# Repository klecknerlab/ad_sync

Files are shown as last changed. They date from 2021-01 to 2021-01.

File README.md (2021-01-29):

# ad_sync
Hardware and software design for a USB-based analog/digital synchronizer board.  Developed by the MUVI and Kleckner Labs at UC Merced.

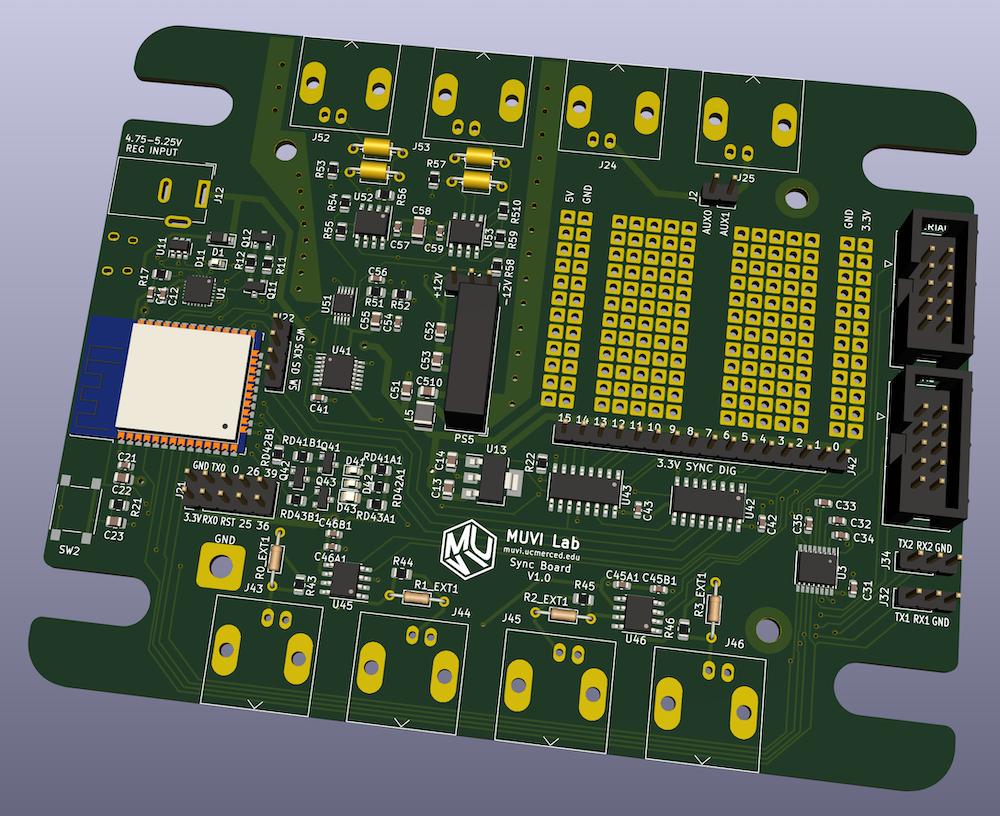
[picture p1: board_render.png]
Board Render


## Description
This project is intended to solve a specific problem: synchronizing a laser scanner and camera setup for 3D volumetric imaging.
To do this, it outputs hardware synchronized digital and analog signals.
The hardware works by converting a single digital bit stream from the on board ESP32 processor to a series of shift registers and a digital-to-analog converter (with ± 10V range).
The update rate is tunable from 30 Hz to 700 kHz, with a ~10 PPM accurate clock (provided by the APLL clock on the ESP32).

The hardware, firmware and software required to run the board is all stored in this repository, with an Apache license.
If you would like to fabricate, modify, or just use these boards, get in touch!

## Features
* 16 synchronized digital outputs.  Four are converted to 5 V and output on external BNC or header pin connections
* 2 synchronized analog outputs, output on BNC or header pins
* 2 auxiliary serial ports (RS-232 levels), tunneled through the main connection, and which can be used to control additional devices
* An RGB output LED, controllable through software, to be used as an indicator light
* A small on-board prototyping area, to add additional functionality
* Pin headers for various on board signals, including unused GPIO ports on the microcontroller.  (These are not usable without a firmware modification.)
* Everything is controlled through a USB port *or* Bluetooth conncection, with simple serial commands.  (To enable bluetooth, use `set_bt_name.py`.)
* In the future, a firmware update may also provide a wifi connection option; the microcontroller is capable of this but the feature has not been coded)

## Project Progress
* [x] Initial board schematics
* [x] Fabricate test hardware
* [x] Feature complete firmware
* [x] USB communications
* [x] Python driver
* [ ] Wifi connection
* [x] Bluetooth connection
* [x] Aux. serial port connections
* [x] Experimental testing and validation
* [x] Synchronizer GUI

## Contents
This project contains four directories:
* `hardware`: the hardware schematics and PCB layout.
* `hardware_fab`: the PCB design output files, which can be sent directly to a board fabricator.
* `firmware`: the Arduino/C++ firmware for the driver board, as a PlatformIO project.  (Note: currently in alpha status.)
* `ad_sync`: a Python library to interface with the board through USB. (Note: currently empty.)

## Python Interface
The device is most easily controlled with the provided Python library.
All of the functions are illustrated in `test.py`, located in this directory.

All of the functions in the communication protocol (described below), also have a corresponding python method with a similar or identical name.

On some OS's you may need to install drivers for the USB chip on the board ([Sillabs CP2104](https://www.silabs.com/developers/usb-to-uart-bridge-vcp-drivers).)

## Description of Synchronized Outputs
The synchronized outputs are fed from an internal memory of up to 16384 samples.
Each sample is a 32 bit unsigned integer.
The high 16 bits are the digital channels, and the low 16 bits are an analog sample.
Typically, the analog sample should contain the full data range (0-65535), and can be dynamically scaled as the signal is generated.
(This way you don't need to upload entirely new data to offset or rescale the analog signal.)

To specify an output, you first upload an arbitrary amount of data (in Python, use the `write_ad` method).
You then tell the device where to read from in memory, by specifying a start address and number of samples (`addr` method).
Additionally, you can specify the output rate in samples/s (`rate` method).

Finally, you can specify that certain digital channels are triggered.
Triggered channels will remain low until a trigger is specified (`trigger` method).
Note that the trigger always starts on the beginning of an output cycle, and can be for one or more cycles.

## Communication Protocol
Although the Python library is convenient, it is also possible to talk to the board directly with serial commands through the USB interface (and eventually: bluetooth and wifi, which will use a serial bridge).

**Command structure:** one to three "words", at most four letters each, followed by 0-3 integers.  Some commands are also followed by arbitrary length binary data.  
All commands are terminated with a linefeed character (`⏎`; this is equivalent to `"\n"` in Python or C).  

The format for binary appended data is `>[number of bytes]>[binary data]`, and should followed by a line feed character.

Note that if the word is longer than 4 letters the extra letters are ignored.
In other words `SYNC AVAIL` is the same as `SYNC AVAI` (or even `SYNC AVAILABLE` if you prefer).  
Lower case letters are converted to upper case internally (i.e. `SynC AvAiXXX` is also equivalent.)

Unless specified otherwise, commands return `ok.⏎` on success.
Error strings will always begin with `ERROR:` and end with `⏎`.

*Note:* For the command words `ANA0`, `ANA1`, `SER1`, and `SER2` there is no space between the letters and number -- this number is part of the command, not an argument!
(If you're wondering why the serial numbering starts with 1: this is because serial 0 is the USB connection.)

### List of Serial Commands
Parameters are specified in square brackets, and correspond to unsigned integers (exception: commands which have an `ON/OFF` option).

**Misc Commands**
* `*IDN⏎`: Returns the identification string for the synchronizer.  (Presently: `USB analog/digital synchronizer (version 1.0)⏎`)
* `LED [r] [g] [b]⏎`: Set the color of the RGB indicator LED.  Each value should be 0-255, and the output is gamma corrected.

**Sync Output Commands**
* `SYNC STAT⏎`: Outputs statistics on the sync DMA buffer output.  Used for debugging, but shouldn't normally be needed.
* `SYNC WRITE [addr] >[n]>[binary data]⏎`: Write synchronous data starting at indicated address (addr < 16384).  
    - Each data point is four bytes, or a uint32.  The highest two bytes are the digital outputs for that sample and the lowest two bytes are the analog signal.  Note that the microcontroller is little-endian, thus the byte order should be `[analog low][analog high][digital low][digital high]`.  
    - The data written should have a length which is a multiple of 4 bytes, but this is not enforced!  (A warning will be issued if this condition is not met.)  There is no padding between samples, and you can upload as many as you want at once.
    - Ideally, the analog data should span the full 0--65535 range.  The amplitude and offset of the output can be controlled with the `ANA[0/1] SCALE` command, so that you don't have to reupload data to rescale the analog output.
* `SYNC [START/STOP]⏎`:
    - Start/stop the synchronous digital outputs by enabling or disabling the shift register outputs and stopping the sync updates.
    - When stopped, the analog channels will default to the values set by `ANA[0/1] SET`.
* `SYNC MODE [analog mode] [digital mode (optional)]⏎`: Set the mode of the sync output.  
	- Analog mode options:
		- `0`: No sync analog output; each channel goes to the default (set w/ `ANA[0/1] SET`)
		- `1`: Analog 0 streams from sync data, analog 1 fixed value (default)
		- `2`: Analog 1 streams from sync data, analog 0 fixed value
		- `3`: Both channels stream, alternating updates.  Even sync data addresses go to analog 0, odd address to analog 1.  Note that this halves the update rate of each channel, relative to the digital signals.
	- Digital mode options:
		- `0`: All 16 outputs derived from sync data (default)
		- `1`: "Or" mode.  Channels 0-7 are logical "or"ed with channels 8-15.  8-15 have the normal output.  (Can be used to superimpose triggered and non-triggered signals.)
        - `2`: "Swap" mode.  Channels 0-7 swapped with 8-15.  (Can be used to switch the
            outputs w/o a reupload.)
        - `3': "Swap-Or" mode.  Apply the swap and then the or operation.
* `SYNC ADDR [addr] [count]⏎`: Change the start address and number of data points for a period of the sync output.
* `SYNC ADDR⏎`: Returns the current sync mode (`SYNC CYCLE [addr] [count]⏎`)
* `SYNC RATE [rate Hz] [rate mHz (optional)]⏎`:
    - Change the synchronous output rate, specified in Hz, with any optional millihertz addition.  (i.e. 100.5 Hz would be specified as `SYNC RATE 100 005⏎` or `SYNC RATE 100 5⏎`.)  Valid values are from 30 to 700000.  
    - Replies with `SYNC RATE = [samples/s] Hz⏎`.  Note that [samples/s] will here be floating point, and reflects the actual frequency as set by the device (will likely be *slightly* different than the requested value)
    - Accuracy/precision is ~10 PPM, as determined by main clock accuracy.
* `ANA[0/1] SCALE [scale] [offset]⏎`:
    - Change the output scale and offset of this channel.  Each scale/offset should be from 0-65536 and covers the range of -10 to 10 V.  
    - `scale` indicates the peak to peak amplitude of the signal (65536 = 20 V peak-to-peak, 3277 = 1.0000 V peak-to-peak)
    - `offset` is the minimum value of the signal (0 = -10 V, 65536 = 10V, 32768 = 0V.)  
    - *Note:* the above scaling assumes the input waveform goes from 0-65535 in the sync data.  If it does not, it will be proportionally smaller.
* `ANA[0/1] SET [value]⏎`:
    - Directly set the analog output value for one of the channels (0=-10V, 65536 = +10V).  No scaling or offset is applied.  
    - *Note 1:* Command ignored if this channel is currently updating synchronously.  
    - *Note 2:* Updating while the sync is running on the other channel will introduce a one sample skip in the output of the synced channel.

**Serial Commands**
* `SER[1/2] WRITE >[n]>[binary data]⏎`: Write `n` bytes to serial port 1/2.  Replies with: `Wrote [n] bytes of data to serial [1/2].⏎`
* `SER[1/2] READ [n (optional)]⏎`:
    - Read at most `n` bytes of data from serial port 1/2  
    - If `n` is not specified (or `n` is greater than the amount of available data), return all available data.  
    - Call is non-blocking: it will not wait for data to be available
    - Reply format is `>[n]>[n bytes of binary]⏎`  
* `SER[1/2] AVAIL⏎`: Return the number of bytes available to be read at that serial port.  Reply format: `[n]⏎`
* `SER[1/2] FLUSH⏎`: Flush the read buffer for a serial port.
* `SER[1/2] RATE [baud rate]⏎`:
    - Set the baud rate for a serial port  
    - The serial format is always 8 bits with a start and stop bit.  (This could be changed by altering the firmware, if needed.)
    - *Note:* Changing the Baud rate of Serial Port 1 will cause an output glitch on the sync outputs.  Unfortunately this is a hardware bug on the microcontroller, which is not correctable!

**Trigger Commands**
* `TRIGER MASK [bit mask]⏎`: A bit mask indicated if each digital output channel is triggered.  Triggered channels output low until triggered.
* `TRIGER [cycles (optional)]⏎`: Activate the trigger for the specified number of cycles.  `cycles=1` is the default.  Note that there may be a delay of up to 256 samples in outputting a triggered signal, due to the output buffering.  Also, triggers always begin at the beginning of a cycle.

**Bluetooth Commands**
* `BLUETOOTH >[n]>[bluetooth name]⏎`:
    - Set the name of the bluetooth device, and enables it
    - Name will be saved to internal flash storage, and will remain after a reboot
    - Name needs to be sent as binary, should be <= 64 bytes (or an error is raised)
    - Replies with `Bluetooth enabled with name: [bluetooth name]⏎`
    - Setting the name to an empty string disables the device (e.g. `BLUETOOTH⏎`)

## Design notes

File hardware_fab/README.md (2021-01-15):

This directory contains the files for fabricating the physical board.
The original version (V1, V1 rev. 2) was fabricated using [JLCPCB](https://jlcpcb.com/), which provides a low cost PCB assembly service.
(5 boards + components ~ $120.)
**If you are going to have these fabricated, you should use the rev. 2 version, which fixes a problem with one of the chip connections!**

All files needed to fabricate the board are in this directory, note that there are two versions of the component placement file -- the one ending in `pos-fixed.csv` has the rotations fixed to JLCPCB's specifications, and this is the file you should use for this board manufacturer.  The similarly named file without the `-fixed` is the raw part placement output from KiCad.

In addition to the surface mount components (which can be installed by JLCPCB), there are a number of through hole components which need to be manually attached.
These are listed below, along with links to Digikey or Amazon to purchase them.
Note that many of these are optional.  
Also not listed are headers for connecting to the peripherial outputs near the center of the board: these are all standard 0.1" pin headers.

**Mandatory Components:**
* Micro-USB connector (1 per board: [Amphenol 10103594-0001LF](https://www.digikey.com/en/products/detail/amphenol-icc-fci/10103594-0001LF/2350351?s=N4IgTCBcDaIIwAZEGYCsBOALCAugXyA))
* DC-DC converter (1 per board: [CUI PDME1-S5-D12-S](https://www.digikey.com/en/products/detail/cui-inc/PDME1-S5-D12-S/10229857) or equivalent)

**Output Connectors:**  (Note: the 8 main outputs are designed to be BNC jacks, but the holes on the board also support attaching a 0.1" header.)
* BNC (up to 8 per board: [TE connectivity 1-1337543-0](https://www.digikey.com/en/products/detail/te-connectivity-amp-connectors/1-1337543-0/1755940) or equivalent.)
* Alternate: 2 pin polarized right angle header (up to 8 per board: [Adam Tech LHA-02-TRB](https://www.digikey.com/en/products/detail/adam-tech/LHA-02-TRB/9830340)) (Mating plug: [Adam Tech MTD-A-02-D-2](https://www.digikey.com/en/products/detail/adam-tech/MTD-A-02-D-2/9830865))
* Serial outputs: 10 pin IDC connectors (up to 2 per board: [On Shore 302-S101](https://www.digikey.com/en/products/detail/on-shore-technology-inc/302-S101/2178422))
* IDC -> DB9 serial connectors (2 per board: [standard DB9 to 10 pin motherboard connector](https://www.amazon.com/CablesOnline-10-Pin-Motherboard-Adapter-AD-I01/dp/B077F2WDZ7/))

**Stand-offs:**
* 1/4"-20 x 1" for mounting the board to an optical table (4 per board: [Essentra 15TSP035](https://www.digikey.com/en/products/detail/essentra-components/15TSP035/11639005))
* 4-40 x 5/8" for mounting a protective top panel (4 per board: [RAF 2059-440-AL](https://www.digikey.com/en/products/detail/raf-electronic-hardware/2059-440-AL/7680412))

**Misc. Optional:**
* Power jack -- only needed if you aren't powering through USB (1 per board: [Wurth 	
694106301002](https://www.digikey.com/en/products/detail/w%C3%BCrth-elektronik/694106301002/5047522))
* Filter capacitors: the analog output amplifiers have empty slots for a through hole capacitor.  
The amplifier resistor is 120 kOhm, so 100 pF gives a -3dB frequency of 13.3 KHz.  
There is already 30 pF attached to the output (CF3/CF13) giving a 44 kHz cutoff; if higher speeds are required you could remove these resistors, but this is not recommended.
If you would like to provide additional filtering, a capacitor could be attachd to CF2/CF12.

* Output resistors: the digital outputs come with a surface mount 50 Ohm resistor installed.  If you would like a different output resistance, you can remove this resistor and add a through hole resistor next to the BNC output.  In most cases this should not be needed.

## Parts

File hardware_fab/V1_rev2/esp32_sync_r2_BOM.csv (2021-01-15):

Comment | Designator | Footprint | LCSC
0.1UF/50V | C11,C21,C31,C32,C33,C34,C35,C41,C42,C43,C44,C46,C54,C57,C59 | Capacitor_SMD:C_0603_1608Metric | C14663
4.7UF/16V | C12,C45,C47 | Capacitor_SMD:C_0603_1608Metric | C19666
22UF/25V | C13,C14,C22,C52,C53 | Capacitor_SMD:C_0805_2012Metric | C45783
1UF/50V | C23 | Capacitor_SMD:C_0805_2012Metric | C28323
4.7UF/25V | C51,C510 | Capacitor_SMD:C_0805_2012Metric | C1779
100PF/50V | C55 | Capacitor_SMD:C_0805_2012Metric | C1790
0.22UF/25V | C56 | Capacitor_SMD:C_0603_1608Metric | C21120
10UF/50V | C58 | Capacitor_SMD:C_1206_3216Metric | C13585
100pF | CF1,CF2,CF11,CF12 | Capacitor_THT:C_Axial_L3.8mm_D2.6mm_P7.50mm_Horizontal
30PF/50V | CF3,CF13 | Capacitor_SMD:C_0603_1608Metric | C22397
B5819W | D1 | Diode_SMD:D_SOD-123 | C8598
RED | D11,D41 | LED_SMD:LED_0603_1608Metric | C2286
GREEN | D42,D44 | LED_SMD:LED_0603_1608Metric | C72043
BLUE | D43 | LED_SMD:LED_0805_2012Metric | C2293
USB_B_Micro | J11 | Connector_USB:USB_Micro-B_Amphenol_10103594-0001LF_Horizontal
Barrel_Jack | J12 | Connector_BarrelJack:BarrelJack_Wuerth_6941xx301002
Conn_01x02_Male | J2 | Connector_PinHeader_2.54mm:PinHeader_1x02_P2.54mm_Vertical
GPIO | J21 | Connector_PinHeader_2.54mm:PinHeader_2x05_P2.54mm_Vertical
I2S | J22 | Connector_PinHeader_2.54mm:PinHeader_1x05_P2.54mm_Vertical
AUX0 | J24 | Connector_Coaxial:BNC_Amphenol_B6252HB-NPP3G-50_Horizontal
AUX1 | J25 | Connector_Coaxial:BNC_Amphenol_B6252HB-NPP3G-50_Horizontal
IDC SER | J31,J33 | Connector_IDC:IDC-Header_2x05_P2.54mm_Vertical
SER1 | J32 | Connector_PinHeader_2.54mm:PinHeader_1x03_P2.54mm_Vertical
SER2 | J34 | Connector_PinHeader_2.54mm:PinHeader_1x03_P2.54mm_Vertical
DS_3.3V | J42 | Connector_PinHeader_2.54mm:PinHeader_1x16_P2.54mm_Vertical
DS0_EXT | J43 | Connector_Coaxial:BNC_Amphenol_B6252HB-NPP3G-50_Horizontal
DS1_EXT | J44 | Connector_Coaxial:BNC_Amphenol_B6252HB-NPP3G-50_Horizontal
DS2_EXT | J45 | Connector_Coaxial:BNC_Amphenol_B6252HB-NPP3G-50_Horizontal
DS3_EXT | J46 | Connector_Coaxial:BNC_Amphenol_B6252HB-NPP3G-50_Horizontal
AV | J51 | Connector_PinHeader_2.54mm:PinHeader_1x03_P2.54mm_Vertical
AS0_EXT | J52 | Connector_Coaxial:BNC_Amphenol_B6252HB-NPP3G-50_Horizontal
AS1_EXT | J53 | Connector_Coaxial:BNC_Amphenol_B6252HB-NPP3G-50_Horizontal
6.8UH/530mA | L5 | Inductor_SMD:L_1210_3225Metric | C87558
PDME1-S5-D12-S | PS5 | Converter_DCDC:Converter_DCDC_XP_POWER-IAxxxxS_THT
S8050 | Q11,Q12,Q41,Q42,Q43,Q44 | Package_TO_SOT_SMD:SOT-23 | C2146
10k | R11,R12,R21,R22 | Resistor_SMD:R_0805_2012Metric | C17414
1k | R17 | Resistor_SMD:R_0805_2012Metric | C17513
47 | R43,R44,R45,R46 | Resistor_SMD:R_0805_2012Metric | C17714
120K/0.1% | R53,R56,R57,R510 | Resistor_SMD:R_0805_2012Metric | C141893
15K/0.1% | R51,R52,R54,R55,R58,R59 | Resistor_SMD:R_0805_2012Metric | C86866
150 | RD41 | Resistor_SMD:R_0805_2012Metric | C17471
4.7K | RD42,RD44,RD46,RD48 | Resistor_SMD:R_0805_2012Metric | C17673
82 | RD43,RD47 | Resistor_SMD:R_0805_2012Metric | C17841
100 | RD45 | Resistor_SMD:R_0805_2012Metric | C17408
- | RO0,RO1,RO2,RO3 | Resistor_THT:R_Axial_DIN0204_L3.6mm_D1.6mm_P7.62mm_Horizontal
RESET | SW2 | Button_Switch_SMD:SW_Push_1P1T_NO_6x6mm_H9.5mm | C136669
CP2104 | U1 | Package_DFN_QFN:QFN-24-1EP_4x4mm_P0.5mm_EP2.6x2.6mm | C47742
SRV05-4 | U11 | Package_TO_SOT_SMD:SOT-23-6 | C85364
AMS1117-3.3 | U13 | Package_TO_SOT_SMD:SOT-223 | C6186
ESP32-WROOM-32D | U2 | RF_Module:ESP32-WROOM-32 | C473012
SP3232 | U3 | Package_SO:HTSSOP-16-1EP_4.4x5mm_P0.65mm_EP3.4x5mm | C13482
74AHC04 | U41 | Package_SO:TSSOP-14_4.4x5mm_P0.65mm | C6936
74HC595 | U42,U43 | Package_SO:SOIC-16_3.9x9.9mm_P1.27mm | C5947
TC4427 | U45,U46 | Package_SO:SOIC-8_3.9x4.9mm_P1.27mm | C144205
DAC8562SDGSR | U51 | Package_SO:VSSOP-10_3x3mm_P0.5mm | C127965
NE5532 | U52,U53 | Package_SO:SOIC-8_3.9x4.9mm_P1.27mm | C7426

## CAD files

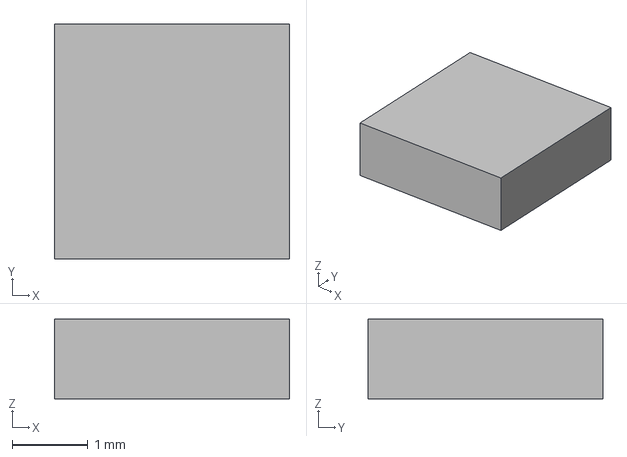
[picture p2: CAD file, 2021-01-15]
hardware/DAC8562/eec.models/Texas_Instruments_-_DAC8562SDGSR.step
3.10 x 3.10 x 1.05 mm

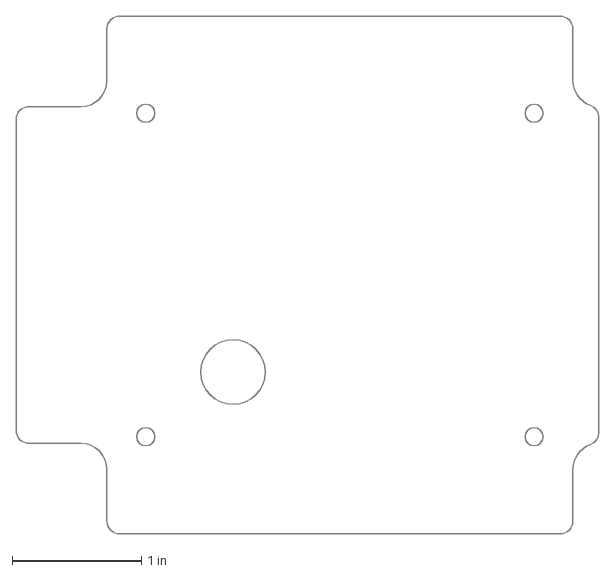
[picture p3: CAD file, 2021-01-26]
hardware_fab/ad_sync.dxf
4.50 x 4.00 in

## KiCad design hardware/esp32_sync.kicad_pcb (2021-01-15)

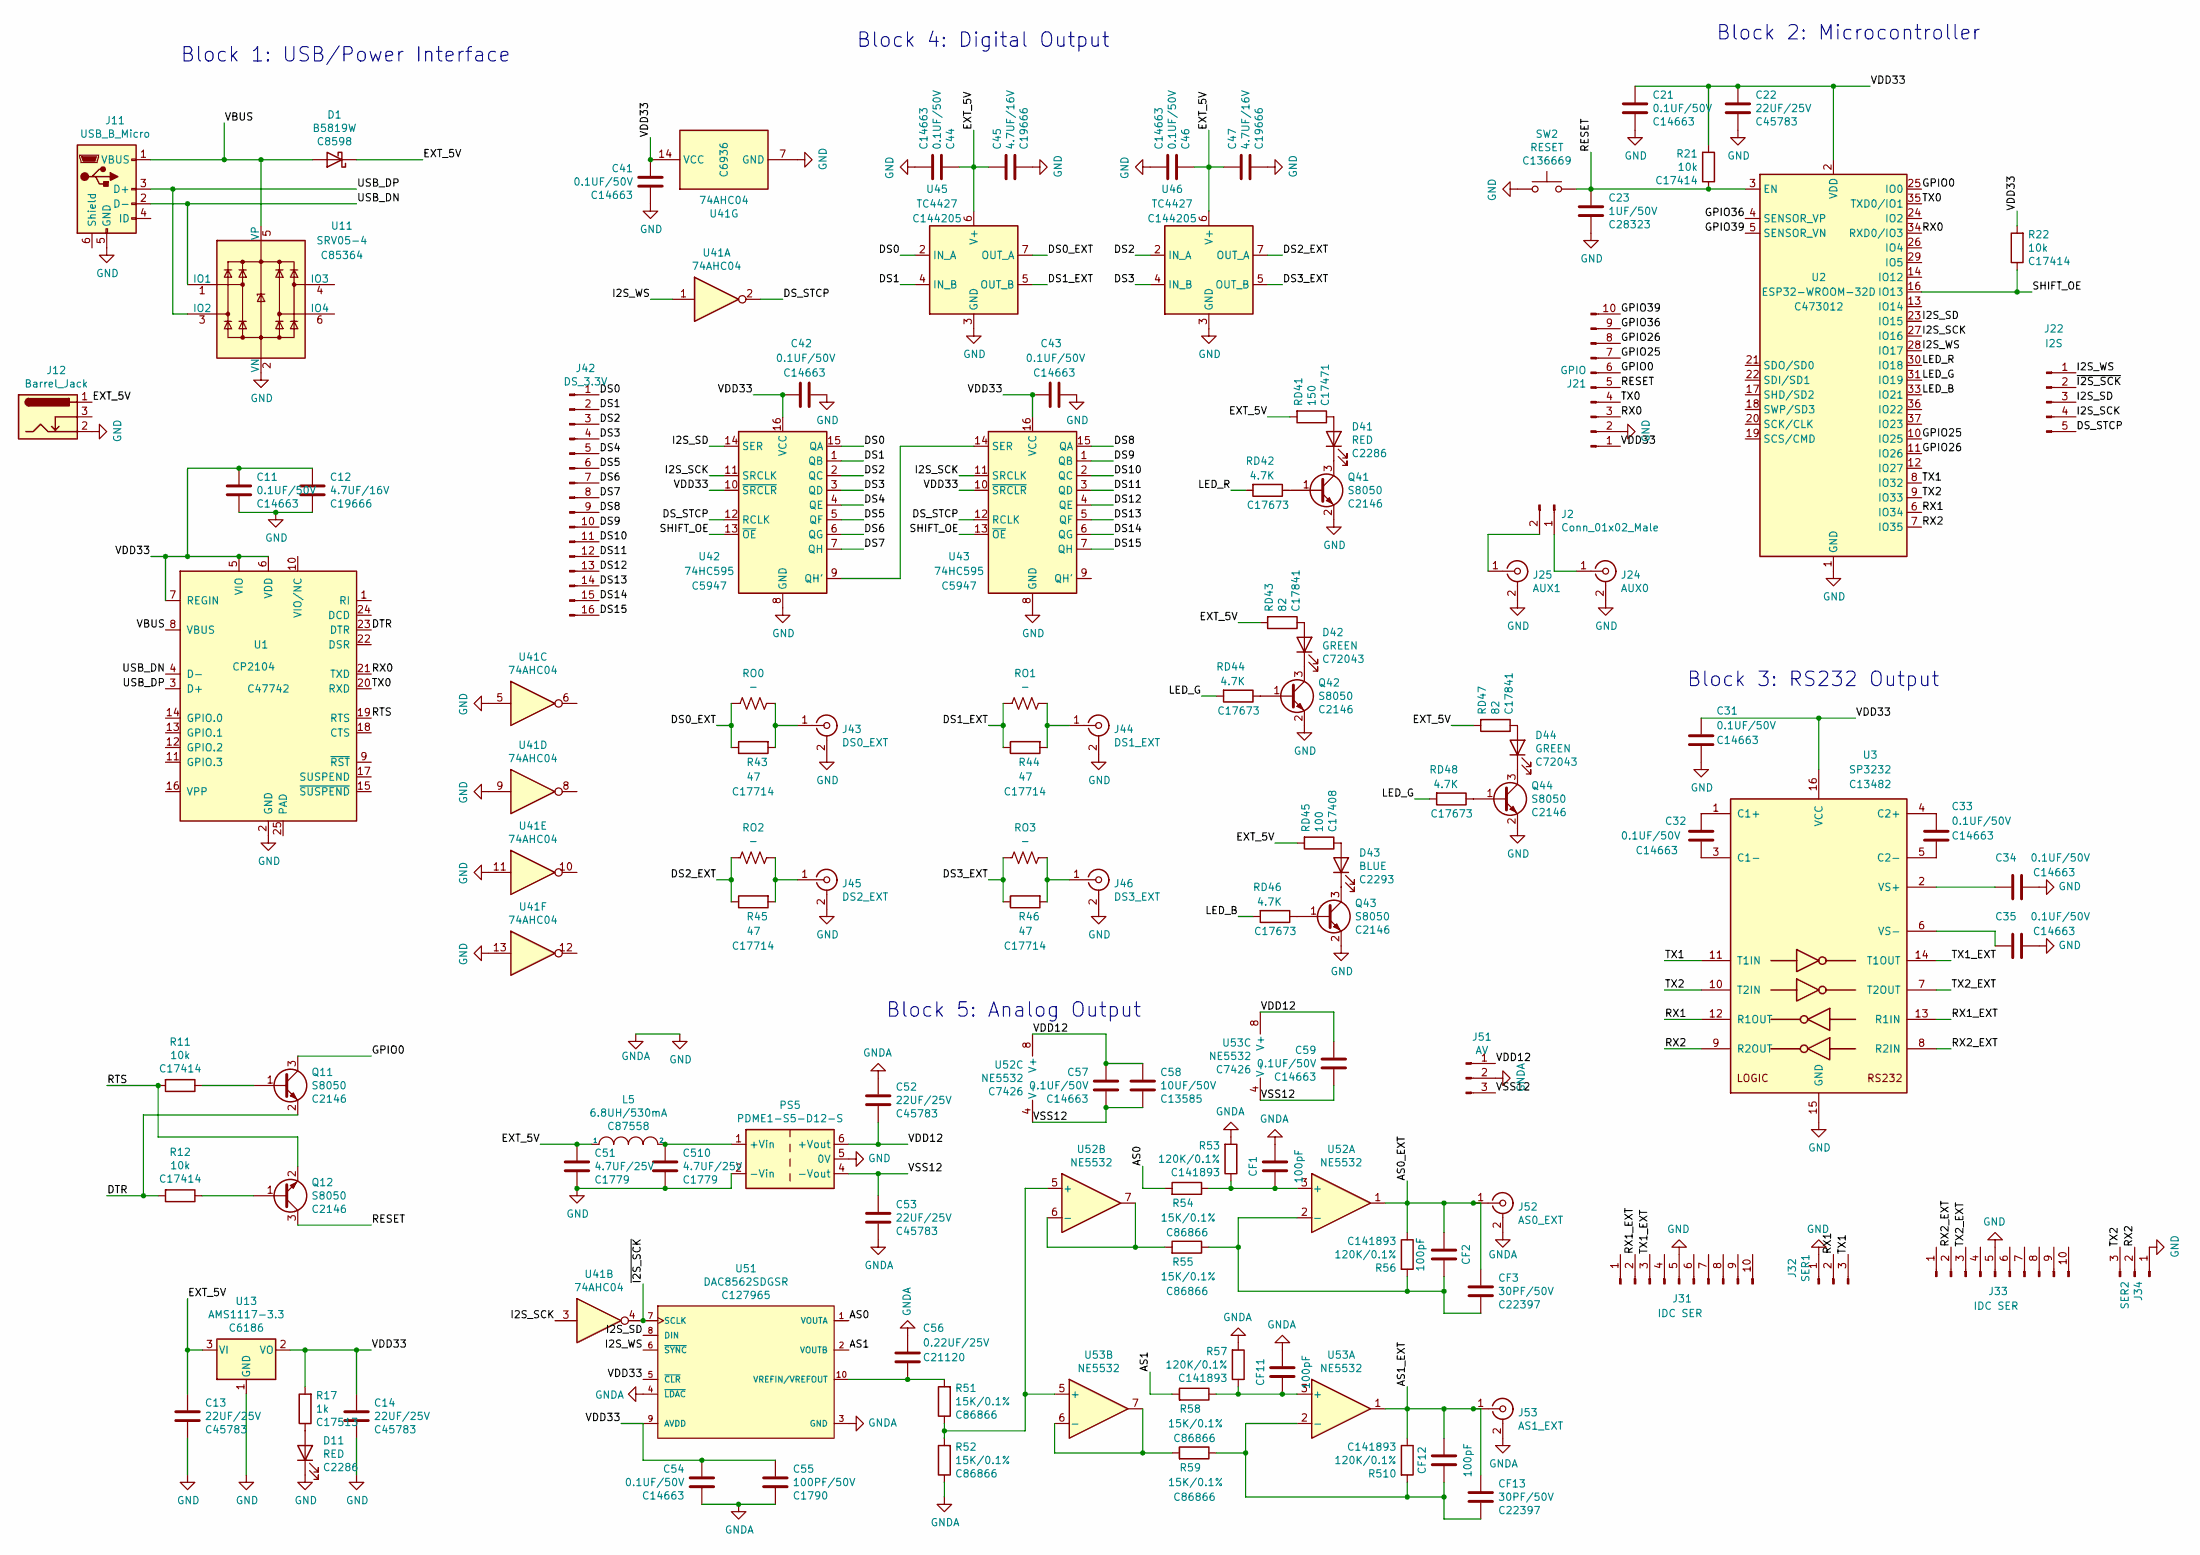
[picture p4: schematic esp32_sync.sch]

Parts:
C11, C21, C31, C32, C33, C34, C35, C41, C42, C43, C44, C46, C54, C57, C59: 0.1UF/50V; C_0603_1608Metric; LCSC C14663
C12, C45, C47: 4.7UF/16V; C_0603_1608Metric; LCSC C19666
C13, C14, C22, C52, C53: 22UF/25V; C_0805_2012Metric; LCSC C45783
C23: 1UF/50V; C_0805_2012Metric; LCSC C28323
C51, C510: 4.7UF/25V; C_0805_2012Metric; LCSC C1779
C55: 100PF/50V; C_0805_2012Metric; LCSC C1790
C56: 0.22UF/25V; C_0603_1608Metric; LCSC C21120
C58: 10UF/50V; C_1206_3216Metric; LCSC C13585
CF1, CF2, CF11, CF12: 100pF; C_Axial_L3.8mm_D2.6mm_P7.50mm_Horizontal
CF3, CF13: 30PF/50V; C_0603_1608Metric; LCSC C22397
D1: B5819W; D_SOD-123; LCSC C8598
D11, D41: RED; LED_0603_1608Metric; LCSC C2286
D42, D44: GREEN; LED_0603_1608Metric; LCSC C72043
D43: BLUE; LED_0805_2012Metric; LCSC C2293
J2: Conn_01x02_Male; PinHeader_1x02_P2.54mm_Vertical
J11: USB_B_Micro; USB_Micro-B_Amphenol_10103594-0001LF_Horizontal
J12: Barrel_Jack; BarrelJack_Wuerth_6941xx301002
J21: GPIO; PinHeader_2x05_P2.54mm_Vertical
J22: I2S; PinHeader_1x05_P2.54mm_Vertical
J24: AUX0; BNC_Amphenol_B6252HB-NPP3G-50_Horizontal
J25: AUX1; BNC_Amphenol_B6252HB-NPP3G-50_Horizontal
J31, J33: IDC SER; IDC-Header_2x05_P2.54mm_Vertical
J32: SER1; PinHeader_1x03_P2.54mm_Vertical
J34: SER2; PinHeader_1x03_P2.54mm_Vertical
J42: DS_3.3V; PinHeader_1x16_P2.54mm_Vertical
J43: DS0_EXT; BNC_Amphenol_B6252HB-NPP3G-50_Horizontal
J44: DS1_EXT; BNC_Amphenol_B6252HB-NPP3G-50_Horizontal
J45: DS2_EXT; BNC_Amphenol_B6252HB-NPP3G-50_Horizontal
J46: DS3_EXT; BNC_Amphenol_B6252HB-NPP3G-50_Horizontal
J51: AV; PinHeader_1x03_P2.54mm_Vertical
J52: AS0_EXT; BNC_Amphenol_B6252HB-NPP3G-50_Horizontal
J53: AS1_EXT; BNC_Amphenol_B6252HB-NPP3G-50_Horizontal
L5: 6.8UH/530mA; L_1210_3225Metric; LCSC C87558
PS5: PDME1-S5-D12-S; Converter_DCDC_XP_POWER-IAxxxxS_THT
Q11, Q12, Q41, Q42, Q43, Q44: S8050; SOT-23; LCSC C2146
R11, R12, R21, R22: 10k; R_0805_2012Metric; LCSC C17414
R17: 1k; R_0805_2012Metric; LCSC C17513
R43, R44, R45, R46: 47; R_0805_2012Metric; LCSC C17714
R51, R52, R54, R55, R58, R59: 15K/0.1%; R_0805_2012Metric; LCSC C86866
R53, R56, R57, R510: 120K/0.1%; R_0805_2012Metric; LCSC C141893
RD41: 150; R_0805_2012Metric; LCSC C17471
RD42, RD44, RD46, RD48: 4.7K; R_0805_2012Metric; LCSC C17673
RD43, RD47: 82; R_0805_2012Metric; LCSC C17841
RD45: 100; R_0805_2012Metric; LCSC C17408
RO0, RO1, RO2, RO3: -; R_Axial_DIN0204_L3.6mm_D1.6mm_P7.62mm_Horizontal
SW2: RESET; SW_Push_1P1T_NO_6x6mm_H9.5mm; LCSC C136669
U1: CP2104; QFN-24-1EP_4x4mm_P0.5mm_EP2.6x2.6mm; LCSC C47742
U2: ESP32-WROOM-32D; ESP32-WROOM-32; LCSC C473012
U3: SP3232; HTSSOP-16-1EP_4.4x5mm_P0.65mm_EP3.4x5mm; LCSC C13482
U11: SRV05-4; SOT-23-6; LCSC C85364
U13: AMS1117-3.3; SOT-223; LCSC C6186
U41: 74AHC04; TSSOP-14_4.4x5mm_P0.65mm
U42, U43: 74HC595; SOIC-16_3.9x9.9mm_P1.27mm; LCSC C5947
U45, U46: TC4427; SOIC-8_3.9x4.9mm_P1.27mm; LCSC C144205
U51: DAC8562SDGSR; VSSOP-10_3x3mm_P0.5mm; LCSC C127965
U52: NE5532; SOIC-8_3.9x4.9mm_P1.27mm; LCSC C7426
U53: NE5532; SOIC-8_3.9x4.9mm_P1.27mm

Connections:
/AS0: R54.2, U51.1 (VOUTA)
/AS0_EXT: CF2.1, CF3.1, J52.1 (In), R56.1, U52.1
/AS1: R58.2, U51.2 (VOUTB)
/AS1_EXT: CF12.2, CF13.1, J53.1 (In), R510.1, U53.1
/DS0: J42.1, U42.15 (QA), U45.2 (IN_A)
/DS0_EXT: R43.1, RO0.2, U45.7 (OUT_A)
/DS1: J42.2, U42.1 (QB), U45.4 (IN_B)
/DS1_EXT: R44.1, RO1.2, U45.5 (OUT_B)
/DS2: J42.3, U42.2 (QC), U46.2 (IN_A)
/DS2_EXT: R45.1, RO2.2, U46.7 (OUT_A)
/DS3: J42.4, U42.3 (QD), U46.4 (IN_B)
/DS3_EXT: R46.1, RO3.2, U46.5 (OUT_B)
/DS4: J42.5, U42.4 (QE)
/DS5: J42.6, U42.5 (QF)
/DS6: J42.7, U42.6 (QG)
/DS7: J42.8, U42.7 (QH)
/DS8: J42.9, U43.15 (QA)
/DS9: J42.10, U43.1 (QB)
/DS10: J42.11, U43.2 (QC)
/DS11: J42.12, U43.3 (QD)
/DS12: J42.13, U43.4 (QE)
/DS13: J42.14, U43.5 (QF)
/DS14: J42.15, U43.6 (QG)
/DS15: J42.16, U43.7 (QH)
/DS_STCP: J22.5, U41.2, U42.12 (RCLK), U43.12 (RCLK)
/DTR: Q11.2 (E), R12.2, U1.23 (DTR)
/EXT_5V: C13.1, C44.1, C45.1, C46.1, C47.1, C51.1, D1.1 (K), J12.1, L5.1, RD41.2, RD43.2, RD45.2, RD47.2, U13.3 (VI), U45.6 (V+), U46.6 (V+)
/GPIO0: J21.6, Q11.3 (C), U2.25 (IO0)
/GPIO25: J21.7, U2.10 (IO25)
/GPIO26: J21.8, U2.11 (IO26)
/GPIO36: J21.9, U2.4 (SENSOR_VP)
/GPIO39: J21.10, U2.5 (SENSOR_VN)
/I2S_SCK: J22.4, U2.27 (IO16), U41.3, U42.11 (SRCLK), U43.11 (SRCLK)
/I2S_SD: J22.3, U2.23 (IO15), U42.14 (SER), U51.8 (DIN)
/I2S_WS: J22.1, U2.28 (IO17), U41.1, U51.6 (~SYNC~)
/LED_B: RD46.2, U2.33 (IO21)
/LED_G: RD44.2, RD48.2, U2.31 (IO19)
/LED_R: RD42.2, U2.30 (IO18)
/RESET: C23.1, J21.5, Q12.3 (C), R21.1, SW2.2, U2.3 (EN)
/RTS: Q12.2 (E), R11.2, U1.19 (RTS)
/RX0: J21.3, U1.21 (TXD), U2.34 (RXD0/IO3)
/RX1: J32.2, U2.6 (IO34), U3.12 (R1OUT)
/RX1_EXT: J31.2, U3.13 (R1IN)
/RX2: J34.2, U2.7 (IO35), U3.9 (R2OUT)
/RX2_EXT: J33.2, U3.8 (R2IN)
/SHIFT_OE: R22.1, U2.16 (IO13), U42.13 (~OE), U43.13 (~OE)
/TX0: J21.4, U1.20 (RXD), U2.35 (TXD0/IO1)
/TX1: J32.3, U2.8 (IO32), U3.11 (T1IN)
/TX1_EXT: J31.3, U3.14 (T1OUT)
/TX2: J34.3, U2.9 (IO33), U3.10 (T2IN)
/TX2_EXT: J33.3, U3.7 (T2OUT)
/USB_DN: J11.2 (D-), U1.4 (D-), U11.1 (IO1)
/USB_DP: J11.3 (D+), U1.3 (D+), U11.3 (IO2)
/VBUS: D1.2 (A), J11.1 (VBUS), U1.8 (VBUS), U11.5 (VP)
/VDD12: C52.2, C57.1, C58.1, C59.1, J51.1, PS5.6 (+Vout), U52.8 (V+), U53.8 (V+)
/VDD33: C11.1, C12.1, C14.1, C21.1, C22.1, C31.1, C41.1, C42.2, C43.2, C54.1, C55.1, J21.1, R17.2, R21.2, R22.2, U1.5 (VIO), U1.6 (VDD), U1.7 (REGIN), U2.2 (VDD), U3.16 (VCC), U13.2 (VO), U41.14 (VCC), U42.10 (~SRCLR), U42.16 (VCC), U43.10 (~SRCLR), U43.16 (VCC), U51.5 (~CLR~), U51.9 (AVDD)
/VSS12: C53.1, C57.2, C58.2, C59.2, J51.3, PS5.4 (-Vout), U52.4 (V-), U53.4 (V-)
/~I2S_SCK: J22.2, U41.4, U51.7 (SCLK)
GND: C11.2, C12.2, C13.2, C14.2, C21.2, C22.2, C23.2, C31.2, C34.2, C35.2, C41.2, C42.1, C43.1, C44.2, C45.2, C46.2, C47.2, C51.2, C52.1, C53.2, C54.2, C55.2, C56.1, C510.2, CF1.2, CF11.2, D11.1 (K), J11.5 (GND), J12.2, J21.2, J24.2 (Ext), J25.2 (Ext), J31.5, J32.1, J33.5, J34.1, J43.2 (Ext), J44.2 (Ext), J45.2 (Ext), J46.2 (Ext), J51.2, J52.2 (Ext), J53.2 (Ext), PS5.2 (-Vin), PS5.5 (0V), Q41.2 (E), Q42.2 (E), Q43.2 (E), Q44.2 (E), R52.1, R53.2, R57.2, SW2.1, U1.2 (GND), U2.1 (GND), U2.15 (GND), U2.38 (GND), U2.39 (GND), U3.15 (GND), U11.2 (VN), U13.1 (GND), U41.5, U41.7 (GND), U41.9, U41.11, U41.13, U42.8 (GND), U43.8 (GND), U45.3 (GND), U46.3 (GND), U51.3 (GND), U51.4 (~LDAC~); also elsewhere on the board
unnamed: C32.1, U3.1 (C1+)
unnamed: C32.2, U3.3 (C1-)
unnamed: C33.1, U3.4 (C2+)
unnamed: C33.2, U3.5 (C2-)
unnamed: C34.1, U3.2 (VS+)
unnamed: C35.1, U3.6 (VS-)
unnamed: C56.2, R51.2, U51.10 (VREFIN/VREFOUT)
unnamed: C510.1, L5.2, PS5.1 (+Vin)
unnamed: CF1.1, R53.1, R54.1, U52.3 (+)
unnamed: CF2.2, CF3.2, R55.1, R56.2, U52.2 (-)
unnamed: CF11.1, R57.1, R58.1, U53.3 (+)
unnamed: CF12.1, CF13.2, R59.1, R510.2, U53.2 (-)
unnamed: D11.2 (A), R17.1
unnamed: D41.1 (K), Q41.3 (C)
unnamed: D41.2 (A), RD41.1
unnamed: D42.1 (K), Q42.3 (C)
unnamed: D42.2 (A), RD43.1
unnamed: D43.1 (K), Q43.3 (C)
unnamed: D43.2 (A), RD45.1
unnamed: D44.1 (K), Q44.3 (C)
unnamed: D44.2 (A), RD47.1
unnamed: J2.1, J24.1 (In)
unnamed: J2.2, J25.1 (In)
unnamed: J43.1 (In), R43.2, RO0.1
unnamed: J44.1 (In), R44.2, RO1.1
unnamed: J45.1 (In), R45.2, RO2.1
unnamed: J46.1 (In), R46.2, RO3.1
unnamed: Q11.1 (B), R11.1
unnamed: Q12.1 (B), R12.1
unnamed: Q41.1 (B), RD42.1
unnamed: Q42.1 (B), RD44.1
unnamed: Q43.1 (B), RD46.1
unnamed: Q44.1 (B), RD48.1
unnamed: R51.1, R52.2, U52.5 (+), U53.5 (+)
unnamed: R55.2, U52.6 (-), U52.7
unnamed: R59.2, U53.6 (-), U53.7
unnamed: U42.9 (QH'), U43.14 (SER)

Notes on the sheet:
Block 1: USB/Power Interface
Block 2: Microcontroller
Block 3: RS232 Output
Block 4: Digital Output
Block 5: Analog Output

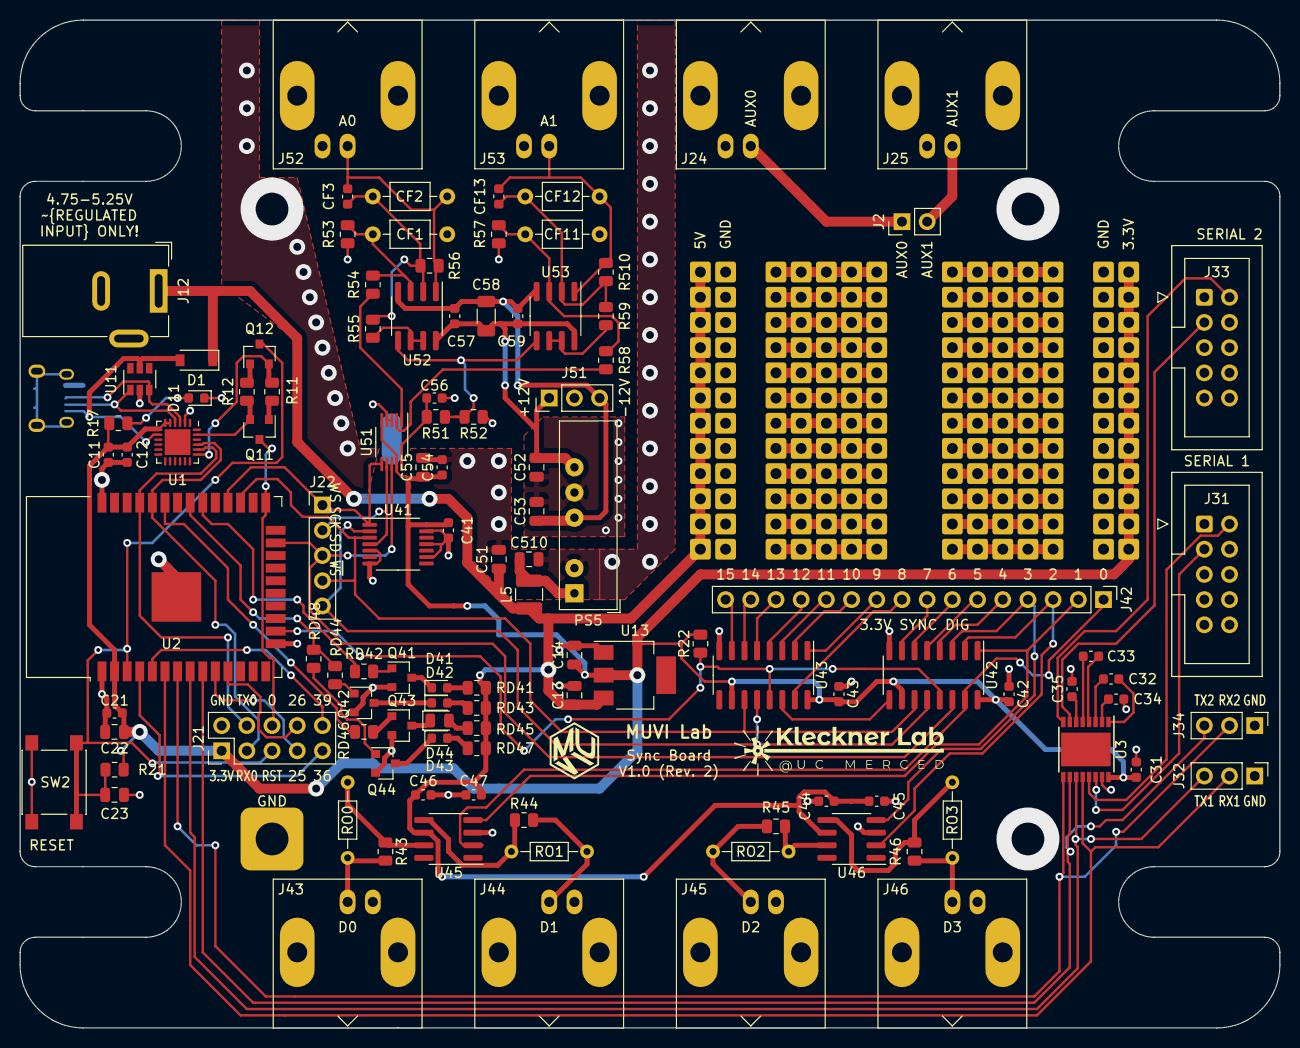
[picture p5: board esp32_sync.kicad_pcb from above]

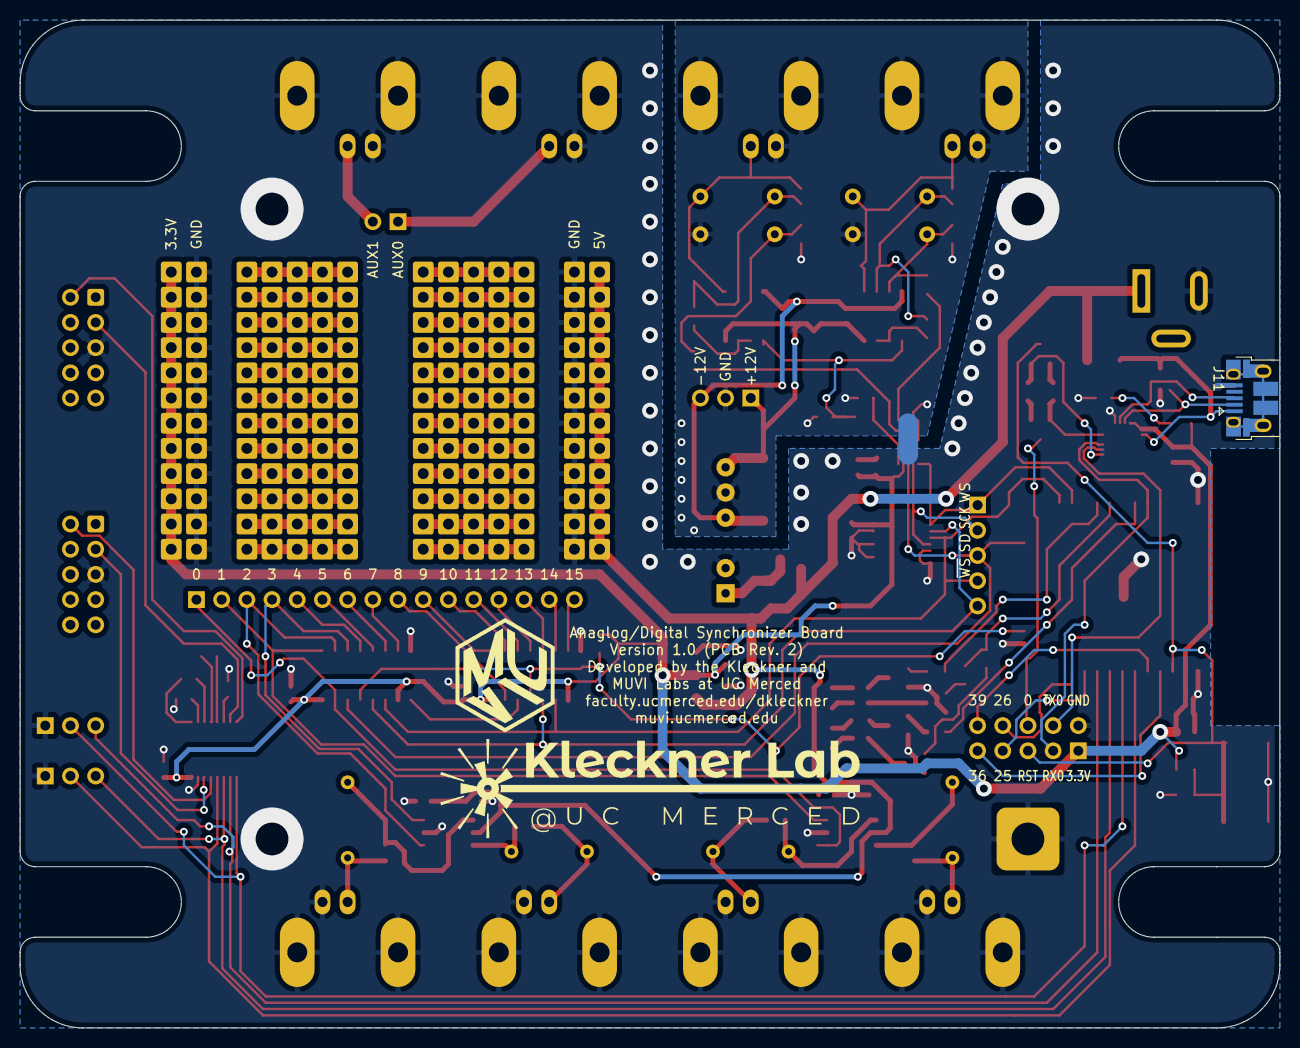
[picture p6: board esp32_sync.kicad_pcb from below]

Board: 2 copper layers, 127.0 x 101.6 mm, 117 parts (2 on the bottom side), 96 nets.

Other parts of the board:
GND: SolderWire-0.1sqmm_1x01_D0.4mm_OD1mm
svg2mod: G***; muvi_5mm
svg2mod#2: G***; muvi_10mm
svg2mod#3: G***; muvi

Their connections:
GND: GND.1; also elsewhere on the board

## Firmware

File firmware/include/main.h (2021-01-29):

#if !defined(MAIN_H)

#define MAIN_H 1
#include <Arduino.h>

// I2S config options
#include "driver/i2s.h"

// Is Bluetooth enabled at all?
#define BLUETOOTH_ENABLED 1

#ifdef BLUETOOTH_ENABLED
    #include "BluetoothSerial.h"
    #if !defined(CONFIG_BT_ENABLED) || !defined(CONFIG_BLUEDROID_ENABLED)
    #error Bluetooth is not enabled! Please run `make menuconfig` to and enable it
    #endif
#endif

// Maximum number of serial characters to process per command queue cycle.
// #define MAX_SERIAL_CHAR_PER_CYCLE   16

// If defined, print debugging messages.  Not recommended for general use!
// #define CMD_DEBUG 1
// #define FREQ_DEBUG 1

// Version numbers.
#define VERSION_MAJOR 1
#define VERSION_MINOR 0


// The output GPIO pin for a variety of functions
#define RX1_PIN         34
#define TX1_PIN         32
#define RX2_PIN         35
#define TX2_PIN         33
#define I2S_CLK_PIN     16
#define I2S_WS_PIN      17
#define I2S_SD_PIN      15
#define OE_PIN          13
#define LED_R_PIN       18
#define LED_G_PIN       19
#define LED_B_PIN       21

const i2s_pin_config_t pin_config = {
    .bck_io_num = I2S_CLK_PIN,
    .ws_io_num = I2S_WS_PIN,
    .data_out_num = I2S_SD_PIN,
    .data_in_num = -1,
};

// LED output gamma -- here matched to typical displays
#define LED_GAMMA       2.2

// The trim is used to scale each output so that max brightness = white
// Output duty cycle is proportional to trim; 65536 is maximum!
// Testing found that with no trim, led 225 255 180 gave white
// R_TRIM = (255/255)^2.2 * 65536
#define LED_R_TRIM      65536
// G_TRIM = (255/255)^2.2 * 65536
#define LED_G_TRIM      65536
// B_TRIM = (180/255)^2.2 * 65536
#define LED_B_TRIM      30457
const uint32_t LED_TRIM[3] = {LED_R_TRIM, LED_G_TRIM, LED_B_TRIM};
const uint8_t LED_PINS[3] = {LED_R_PIN, LED_G_PIN, LED_B_PIN};

// LED outputs a nice sequence of colors on boot, as defined here
#define LED_STARTUP_LEN 5
// Interval is in ms
#define LED_STARTUP_INTERVAL 750 
const uint8_t LED_STARTUP_SEQ[LED_STARTUP_LEN][3] = {
    {  0,   0,   0},
    {  0,   0, 255},
    {  0, 255, 255},
    {225, 255, 255},
    {  0,   0,   0},
};
extern int startup_colors_active;

// The size of various buffers.
#define SER_BUFFER_SIZE 1024 // Used to buffer all inputs/outputs -- this is in addition to the built in serial buffer, which is 64 bytes.
#define SYNC_DATA_SIZE  16384 // Sync data storage.  Larger sizes seem to result in memory errors.
#define I2S_WRITE_BUFFER_SIZE 64 // Used to compute output values


// General purpose macros
#define min(a,b) (((a)<(b))?(a):(b))
#define max(a,b) (((a)>(b))?(a):(b))

// Bit depth of I2S output
// Note: if you need to change this, it will require *many* alterations to other parts of the code!
// (This is just defined for convenience -- don't change it!)
#define I2S_BIT_DEPTH 24

// Globally shared variables and arrays
// Most of these are output settings which need to be modified by the command queue

// LED look up table; used for gamma correction
extern uint16_t LED_LUT[256];

void set_led_color(int r, int g, int b);

// I2S buffer used to write new samples
// extern uint64_t i2s_write_buffer[I2S_WRITE_BUFFER_SIZE]; // Does not need to be global

// Data for the sync outputs
extern uint32_t sync_data[SYNC_DATA_SIZE];

// The start and length of the current cycle
extern int sync_start, sync_cycles;

// Is the sync output active?
extern int sync_active;

// Minimum and maximum frequency, set by the limits of the APLL clock
#define MIN_FREQ 30
#define MAX_FREQ 700000

// Used to compute "sync stat" output
extern uint last_bytes_written, cycles_since_write;
extern unsigned long buffer_update_time, last_sync_update;

// Analog default outputs when not in sync mode
extern uint16_t ana0_set, ana1_set;

// Analog channel flags; bit 0 => ana0, bit 1 -> ana1
// If update is set for a channel, then the "default" value needs to be sent to the DAC
extern int analog_update, analog_sync_mode;

// Used to scale analog output
extern uint32_t ana0_multiplier, ana0_offset, ana1_multiplier, ana1_offset;

// Digital output mode
extern int digital_sync_mode;

// Trigger count
extern int trigger_count;
extern uint32_t trigger_mask;

// Function to change frequency
float sync_freq(float freq);

// Maximum string length for bluetooth serial, to avoid infinite writes
#ifdef BLUETOOTH_ENABLED
    #define SERIAL_BT_MAX_WRITE 1024
    #define BT_NAME_MAX_LENGTH 256
    extern char bt_name[BT_NAME_MAX_LENGTH+1];
#endif
esp_err_t bluetooth_set_name(const char* name);

// Circular buffer class
// This is a non-blocking way of storing serial input/output.
// It will fail silently on overlow, but set the overflow variable.
// Code in "circular_buffer.cpp"
class CircularBuffer {
    public:
        uint8_t buffer[SER_BUFFER_SIZE];
        uint8_t *b_current, *b_end;
        int start, available, overflow;

        CircularBuffer();
        int write(const uint8_t *s);
        int write(const char *s);
        int write(const uint8_t *s, int nbytes);
        int write(const char *s, int nbytes);
        int write(const uint8_t c);
        int from_stream(Stream &stream);
        int to_stream(HardwareSerial &stream);
        #ifdef BLUETOOTH_ENABLED
            int to_stream(BluetoothSerial &stream);
        #endif
        int to_stream(CircularBuffer &buf);
        uint8_t * get_buffer(int * max_data);
        void flush();
};

extern CircularBuffer ser0_output, ser1_input, ser1_output, ser2_input, ser2_output;

#ifdef BLUETOOTH_ENABLED
    extern CircularBuffer serbt_output;
#endif

#endif

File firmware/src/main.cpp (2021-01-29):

// This file includes the setup and loop functions, as well as the serial interaction code.
// The actual commands are processed in "commands.cpp", and the sync data is handled in "sync.cpp"

#include "main.h"
#include "commands.h"
#include "sync.h"
#include "esp_system.h"
#include "nvs_flash.h"
#include "nvs.h"

// Define some globally shared variables/arrays
uint16_t LED_LUT[256];

// Set up the serial input/output buffers
// Note: these are in *addition* to the Arduino serial buffers.
// This provides a non-blocking method for large reads/writes
CircularBuffer ser0_output, ser1_input, ser1_output, ser2_input, ser2_output;

// Bluetooth setup
#ifdef BLUETOOTH_ENABLED
    char bt_name[BT_NAME_MAX_LENGTH+1];
    BluetoothSerial SerialBT;
    static int bt_enabled = 0;
    CircularBuffer serbt_output;
#endif

TaskHandle_t command_task;         

void setup()
{
    // Build LED lookup table for gamma correction
    for (int i=0; i<256; i++) {
        LED_LUT[i] = int(pow((float)i / 256., LED_GAMMA) * 65535.0 + 0.5);
    }

    // Set up LED outputs, and set to start of startup sequence
    for (int i=0; i<3; i++) {
        ledcSetup(i, 5000, 16);
        ledcAttachPin(LED_PINS[i], i);
        ledcWrite(i, (i==0) ? 255 : 0);
    }

    // Set up OE pin, which enables the shift registers
    pinMode(OE_PIN, OUTPUT);
    digitalWrite(OE_PIN, LOW); // Shift registers enabled

    // Set up serial ports
    Serial.begin(921600); // 0 is used for USB communication with host
    Serial1.begin(9600, SERIAL_8N1, RX1_PIN, TX1_PIN); // Ser1
    Serial2.begin(9600, SERIAL_8N1, RX2_PIN, TX2_PIN); // Ser2
    Serial.flush();
    Serial1.flush();
    Serial2.flush();

    // Set up NVS storage.  At present, this is used only for the bluetooth name
    esp_err_t err = nvs_flash_init();
    if (err == ESP_ERR_NVS_NO_FREE_PAGES) {
        // NVS partition was truncated and needs to be erased
        // Retry nvs_flash_init
        ESP_ERROR_CHECK(nvs_flash_erase());
        err = nvs_flash_init();
    }
    ESP_ERROR_CHECK( err );

    #ifdef BLUETOOTH_ENABLED
        nvs_handle nvs;
        size_t bt_name_len = BT_NAME_MAX_LENGTH+1;
        err = nvs_open("bluetooth", NVS_READONLY, &nvs);
        if (err != ESP_OK) {
            Serial.write("ERROR: attempt to open NVS handle failed with '");
            Serial.write(esp_err_to_name(err));
            Serial.write("'\n");
        }

        err = nvs_get_str(nvs, "name", bt_name, &bt_name_len);
        switch (err) {
            case ESP_OK:
                if (bt_name[0]) {
                    SerialBT.begin(bt_name);
                    bt_enabled = 1;
                    Serial.write("Bluetooth connection enabled with name: ");
                    Serial.write(bt_name);
                    Serial.write("\n");
                } else {
                    bt_enabled = 0;
                    Serial.write("Bluetooth disabled; use command 'BLUETOOTH' to initialize.");
                }
                break;
            default:
                Serial.write("Error trying to read bluetooth name from NVS (");
                Serial.write(esp_err_to_name(err));
                Serial.write(")\n");
        }
        nvs_close(nvs);
    #endif

    // Init the sync code (see sync.cpp)
    init_sync();
}

esp_err_t bluetooth_set_name(const char* name) {
    esp_err_t err = ESP_ERR_NOT_SUPPORTED;

    #ifdef BLUETOOTH_ENABLED
        nvs_handle nvs;

        err = nvs_open("bluetooth", NVS_READWRITE, &nvs);
        if (err != ESP_OK) {return err;}

        err = nvs_set_str(nvs, "name", bt_name);
        nvs_close(nvs);

        if (err == ESP_OK) {
            SerialBT.end();
            bt_enabled = 0;
            if (bt_name[0]) {
                SerialBT.begin(bt_name);
                bt_enabled = 1;
            }
        }

    #endif
    return err;
}

// Create a static serial function so we can pass it to a command queue.
// void serial_write(const char* s) {Serial.write(s);}
CommandQueue serial_commands;

#ifdef BLUETOOTH_ENABLED
    CommandQueue serial_bt_commands;
#endif

// Note: multiple command queues can operate simultaneously.
// This is designed to allow for future wifi/bluetooth connection modes.
// If these are added, create a NEW command queue with a corresponding output function as the argument.
// You will then need to add a new hook in the loop function below to feed characters to the command processing.

int startup_colors_active = 1;

void loop()
{
    // This loops processes all the command queues, and updates the DMA for the sync
    // Note that update_sync should return quickly if there is nothing to do; it's better
    //  to run it a lot to avoid corrupting the output.

    // Update the LED with pretty colors on boot.
    if (startup_colors_active) {
        unsigned long t = millis();
        int i = t / LED_STARTUP_INTERVAL;
        if (i >= (LED_STARTUP_LEN-1)) {
            i = LED_STARTUP_LEN - 1;
            set_led_color(
                LED_STARTUP_SEQ[i][0],
                LED_STARTUP_SEQ[i][1],
                LED_STARTUP_SEQ[i][2]
            );
            startup_colors_active = 0;
        } else {
            int r1 = LED_STARTUP_SEQ[i  ][0];
            int r2 = LED_STARTUP_SEQ[i+1][0];
            int g1 = LED_STARTUP_SEQ[i  ][1];
            int g2 = LED_STARTUP_SEQ[i+1][1];
            int b1 = LED_STARTUP_SEQ[i  ][2];
            int b2 = LED_STARTUP_SEQ[i+1][2];
            int m2 = (t * 256) / LED_STARTUP_INTERVAL - i * 256;
            int m1 = 256 - m2;
            set_led_color(
                (m1 * r1 + m2 * r2) >> 8,
                (m1 * g1 + m2 * g2) >> 8,
                (m1 * b1 + m2 * b2) >> 8
            );
        }
    }

    // Process input commands from USB
    for (int i=Serial.available(); i>0; i--) {
        int c = Serial.read();
        if (c >= 0) {serial_commands.process_char((char)c);}
        else {break;}
    }
    update_sync();
    serial_commands.output_buffer.to_stream(Serial);
    update_sync();

    // Procuess input commands from Bluetooth
    #ifdef BLUETOOTH_ENABLED
    if (bt_enabled) {
        for (int i=SerialBT.available(); i>0; i--) {
            int c = SerialBT.read();
            if (c >= 0) {serial_bt_commands.process_char((char)c);}
            else {break;}
        }
        update_sync();
        serial_bt_commands.output_buffer.to_stream(SerialBT);
        update_sync();
    }
    #endif

    // Handle aux serial inputs/outputs
    // Should be pretty fast!
    ser1_output.to_stream(Serial1);
    ser2_output.to_stream(Serial2);
    ser1_input.from_stream(Serial1);
    ser2_input.from_stream(Serial2);

    update_sync();
}


void set_led_color(int r, int g, int b) {
    ledcWrite(0, (LED_LUT[max(min(r, 255), 0)] * LED_TRIM[0]) >> 16);
    ledcWrite(1, (LED_LUT[max(min(g, 255), 0)] * LED_TRIM[1]) >> 16);
    ledcWrite(2, (LED_LUT[max(min(b, 255), 0)] * LED_TRIM[2]) >> 16);
}

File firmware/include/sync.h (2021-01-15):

#if !defined(SYNC_H)

#define SYNC_H 1
#include <Arduino.h>

// The shared sync variables are defined in main.h, since they are also accessed by command.h

// Constants used only by sync.cpp

// The following blocks depend on the DAC on the device.
// The production version uses DAC8562
// The prototype used MCP4822 (becuase I had one lying around!)

#define DAC8562 1
#ifdef DAC8562
    // These are the SPI header bits used for the MCP4822
    // Note: the data is always 16 bits, so we are shifting to the left of that.
    #define DAC_SPI_CH0 (0b011000 << 16)
    #define DAC_SPI_CH1 (0b011001 << 16)

    // These codes are run (in order) after the device is fully booted.
    
    // Internal reference, gain = 2
    #define DAC_SETUP_A 0b001110000000000000000001
    //                    XXCCCAAAddddddddDDDDDDDD
    // Set both DAC to gain = 1
    #define DAC_SETUP_B 0b000000100000000000000011
    //                    XXCCCAAAddddddddDDDDDDDD
    // Disable both LDAC pins
    #define DAC_SETUP_C 0b001100000000000000000011
    //                    XXCCCAAAddddddddDDDDDDDD
    // Power up both DACs
    #define DAC_SETUP_D 0b001000000000000000000011
    //                    XXCCCAAAddddddddDDDDDDDD

    // Bit shift required to align the data.  The buffer is 32 bits, and the data+header is 24 bits
    #define DAC_SHIFT 8

    // Delay in us after boot to try running the setup commands.
    #define DAC_SETUP_DELAY_US 100000
#endif

// #define MCP4822 1
#ifdef MCP4822
    // These are the SPI header bits used for the MCP4822
    // Note: the data is always 16 bits, so we are shifting to the left of that.
    #define DAC_SPI_CH0 (0b0011 << 16)
    #define DAC_SPI_CH1 (0b1011 << 16)
    #define DAC_SETUP_A 0
    #define DAC_SETUP_B 0
    #define DAC_SETUP_C 0
    #define DAC_SETUP_D 0
    // Bit shift required to align the data.  The buffer is 32 bits, and the data+header is 20 bits
    #define DAC_SHIFT 12
    #define DAC_SETUP_DELAY_US 0
#endif

// Output masks for analog and digital data
#define I2S_DIG_MASK (0xFFFFFFFF00000000)
#define I2S_ANA_MASK (0x00000000FFFFFFFF)

#define APLL_MIN 350000000
#define APLL_MAX 560000000
#define APLL_XTAL 40000000
#define NUM_APLL_DIV 36

// Used to get rtc_clk_apll_enable
#include <soc/rtc.h>
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

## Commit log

2021-01-05 Initial commit. (Hardware complete, firmware partial, python library missing.)
    [esp32_sync-BOM.csv, esp32_sync-B_Cu.gbr, esp32_sync-B_Mask.gbr, esp32_sync-B_SilkS.gbr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]
2021-01-05 Added board image.
2021-01-11 Added bluetooth functionality; currently buggy!
2021-01-12 Code cleanup, added startup LED sequence
2021-01-15 Modified firmware for hardware, rev. 2 of PCB.
    [Texas_Instruments_-_DAC8562SDGSR.step, esp32_sync-B_Cu.gbr, esp32_sync-B_Mask.gbr, esp32_sync-B_Paste.gbr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]
2021-01-26 Added top plate drawing, minor fixes
    [ad_sync.dxf]
2021-01-29 Added LED control, reenabled bluetooth
2021-02-24 Added new options to muvi_sync: double pulse, triggered start, cont. frames.
